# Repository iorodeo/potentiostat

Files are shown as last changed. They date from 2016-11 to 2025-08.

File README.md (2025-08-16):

# IO Rodeo Rodeostat 

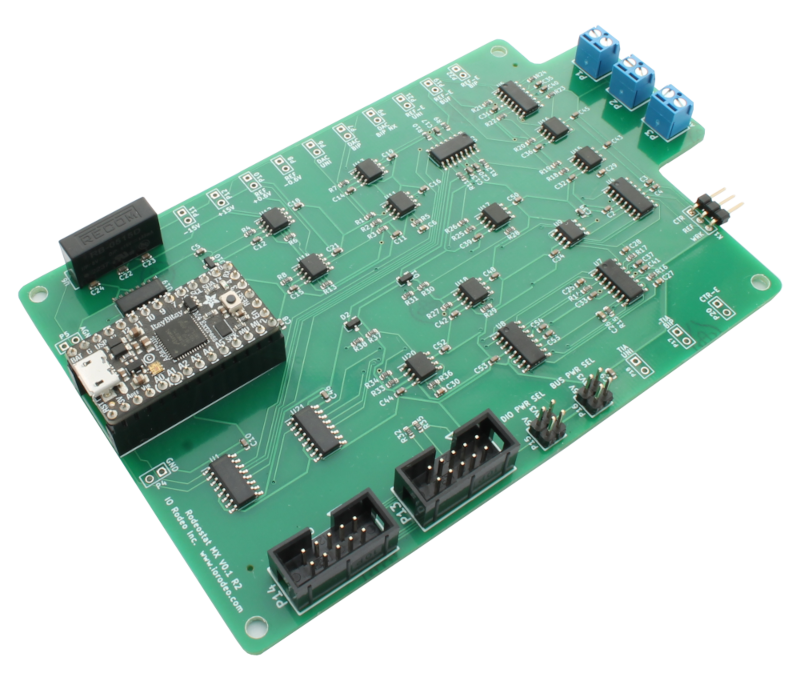
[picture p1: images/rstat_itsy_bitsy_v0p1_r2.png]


Hardware design, firmware and software for IO Rodeo's Rodeostat Potentiostat. 

* Project site: http://potentiostat.iorodeo.com 

## Hardware

* Designed as a shield for  [teensy 3.2 development board](https://www.pjrc.com/teensy/teensy31.html).   
* 12-bit voltage output with four range settings:  +/- 1, 2, 5, 10V
* 16-bit current measurement with four  range settings: +/- 1, 10, 100, 1000 uA ranges
* Can be programmed over USB using the Arduino IDE ([teensyduino](https://www.pjrc.com/teensy/td_download.html)).  
* Expansion headers with DIO, analog inputs, UART, I2C, and SPI 
* [Schematic](https://github.com/iorodeo/potentiostat/releases/download/v0.1/potentiostat_shield_schematic_v0p1r2.pdf)

## Firmware

* Implements many standard voltammetric methods including: 
    - constant voltage, 
    - cyclic voltammetry, 
    - sinusoidal voltammetry,
    - linearsweep voltammetry, 
    - chronoamperometry, 
    - multistep. 
* API for control over USB/Serial using messages in JSON. 
* Easy to extend enabling users to add custom tests. 

## Libraries

* Python 
    - Documentation https://iorodeo.github.io/iorodeo-potentiostat-docs-build/

## Software

* Web app
    - Documentation https://blog.iorodeo.com/rodeostat-software/

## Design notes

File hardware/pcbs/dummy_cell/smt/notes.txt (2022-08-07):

Surface mount right angle header 0.1" pitch.  Part #BG300-03-A-L-A

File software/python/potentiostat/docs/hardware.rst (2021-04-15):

################
Hardware Summary 
################

* teensy 3.2 (32-bit ARM Cortex-M4 72 MHz CPU, 256k Flash, 64k RAM, 2K EEPROM)
* 12-bit voltage output with four available ranges:   ±1, 2, 5, 10V
* 16-bit current measurement with four available ranges: ±1, 10, 100, 1000uA
* Controlled over USB using simple JSON messages  
* Can be programmed over USB using the Arduino IDE (`teensyduino <https://www.pjrc.com/teensy/td_download.html>`_).  
* Expansion headers with DIO, analog inputs, UART, I2C, and SPI 
* Firmware supports many standard voltammetric methods including:
    * constant voltage
    * cyclic voltammetry
    * sinusoidal voltammetry 
    * linear sweep voltammetry
    * chronoamperometry
    * multistep

For a more detailed description of the device hardware see (TODO)

*********
Schematic
*********
`download pdf <https://github.com/iorodeo/potentiostat/releases/download/v0.1/potentiostat_shield_schematic_v0p2r1.pdf>`_

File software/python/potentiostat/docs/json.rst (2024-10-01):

.. _json_ref:

############################
JSON Serial Commands
############################

All messages sent between the Rodeostat and the host PC are sent as serialized
JSON.  This section provides a brief introduction to to these commands and the
associated responses to the command returned by the device. 

.. note::

    The Potentiostat class provides a high level interface implementing this
    protocol - so you don't need to know the details of the JSON serial
    commands in order to use the Rodeostat with Python. We provide the details
    here in order ot enable a more complete understand of how the device
    functions and to assist those who wishing to develop their own custom
    programming interfaces with the Rodeostat. 

The basic form of the commands sent from the host PC to the Rodeostat are JSON
objects with the key "command" whose value specifies the name of the command.
Additional arguments, which are specific to the command, are given as key/value
pairs. The names and number of the required additional arguments are specific 
to each command. 

.. code-block:: json

    {"command": "command name", "arg1": "val1", "arg2": "val2"}

The response from the device, in turn, is a JSON object containing a key named
"success" whose value is a boolean specifying whether or not the command was
successful. If the command was successful the boolean value will be true and
the object will contain a key named "response" whose value contains the
response from the device. The response itself consists of a number of key/value
pairs which are specific to the command. However, reposonse will always contain
the key "command" whose value specifies the name of the command generating the
response. 

.. code-block:: json

    {"success": true, "response", {"command": "command name", "key1": "val1", "key2": "val2"}}

On the other hand if the command was unsuccessful the boolean value will be
false and the object will contain the key "message" whose value contains an
error message from the device. 

.. code-block:: json

    {"success": false, "message": "error message from device", "response": {}}

List of commands
################

getVariant
    Returns a string representing the hardware variant
    
    Form:
    
    .. code-block:: 

        {CommandKey: GetVariantCmd}

    Example command:

    .. code-block:: json
    
        {"command":"getVariant"}

    Example response:
    
    .. code-block:: json
    
        {"success":true,"response":{"command":"getVersion","version":"FW0.0.9"}}

stopTest
    Stops (any) currently running tests

    Form: 

    .. code-block:: 
    
        {CommandKey: StopTestCmd}

    Example command

    .. code-block:: json

        {"command":"stopTest"}

    Example response:

    .. code-block:: json

        {"success":true,"response":{"command":"stopTest"}}

getVolt
    Returns the output voltage setting, i.e, the potential between the working
    and reference electrode. 

    Form: 
    
    .. code-block:: 
    
        {CommandKey: GetVoltCmd}

    Example command:

    .. code-block:: json

        {"command":"getVolt"}

    Response:

    .. code-block:: json

        {"success":true,"response":{"command":"getVolt","v":-0.000244}}

setVolt
    Sets the output voltage setting, i.e., the potential between the working
    and reference electrode. 

    Form: 
    
    .. code-block:: 
    
        {CommandKey: SetVoltCmd, VoltKey: volt}

    Example command:

    .. code-block:: json

        {"command":"setVolt", "v": 0.5}

    Example response:

    .. code-block:: json

        {"success":true,"response":{"command":"setVolt","v":0.499878}}

getCurr
    Gets an immediate measurement of the working electrode current. 

    Form: 
    
    .. code-block:: 
    
        {CommandKey: GetCurrCmd}

    Example command:

    .. code-block:: json

        {"command": "getCurr"}

    Example response:

    .. code-block:: json

        {"success":true,"response":{"command":"getCurr","i":-0.095238}}

getRefVolt
    Gets an immediate measurement of the potential between the working and
    reference electrode. 

    Form: 
    .. code-block:: 
        
        {CommandKey: GetRefVoltCmd}

    Example command:
    
    .. code-block:: json

        {"command": "getRefVolt"}

    Example response:
    
    .. code-block:: json
    
        {"success":true,"response":{"command":"getRefVolt","r":0.761661}}

getParam
    Returns the current values of the parameters for the specified
    voltammetric test. 

    Form: 
    
    .. code-block:: 
    
        {CommandKey: GetParamCmd, TestKey: testname} 

    Example command:

    .. code-block:: json
    
        {"command": "getParam", "test": "cyclic"}

    Example response:
    
    .. code-block:: json
    
        { 
            "success":true,
            "response": {
                "command":"getParam",
                "test":"cyclic",
                "param":{
                    "quietValue":0,
                    "quietTime":0,
                    "amplitude":1,
                    "offset":0,
                    "period":1000,
                    "numCycles":10,
                    "shift":0 
                }
            }
        }

setParam
    Sets the parameters for the specified voltammetric test.

    Form: 
    
    .. code-block:: 

        {CommandKey: SetParamCmd, TestKey: testname, ParamKey: param}

    Example command: 
    
    .. code-block:: json
    
        {
            "command": "setParam",  
            "test": "cyclic",  
            "param": {
                "quietValue": -0.1,
                "quietTime": 1000,
                "amplitude": 1.5,
                "offset": 0,
                "period": 1000,
                "numCycles": 10,
                "shift": 0
            }
        }

    Example response:
    
    .. code-block:: json
    
        {
            "success": true,
            "response": {
                "command": "setParam",
                "test": "cyclic",
                "param": {
                    "quietValue": -0.1,
                    "quietTime": 1000,
                    "amplitude": 1.5,
                    "offset": 0,
                    "period": 1000,
                    "numCycles": 10, 
                    "shift": 0
                }
            }
        }

setVoltRange
    Sets the output voltage range (V)- used when setting output voltage
    manually.

    Form: 

    .. code-block:: 

        {CommandKey: SetVoltRangeCmd, VoltRangeKey: volt_range} 

    Example command:
    
    .. code-block:: json
    
        {"command":"setVoltRange", "voltRange": "2V"}

    Example response:
    
    .. code-block:: json
    
        {"success":true,"response":{"command":"setVoltRange","voltRange":"2V"}}

getVoltRange
    Gets the current value for the output voltage range (V).

    Form: 
    
    .. code-block:: 
        
        {CommandKey: GetVoltRangeCmd}

    Example command:
    
    .. code-block:: json
    
        {"command":"getVoltRange"}

    Example response:
    
    .. code-block:: json
    
        {"success":true,"response":{"command":"getVoltRange","voltRange":"2V"}}

setCurrRange
    Sets the range setting for measuring working electrode (uA).

    Form: 
    
    .. code-block:: 
    
        {CommandKey: SetCurrRangeCmd, CurrRangeKey: curr_range}

    Example command:
    
    .. code-block:: json
    
        {"command":"setCurrRange", "currRange": "100uA"}

    Example response:
    
    .. code-block:: json
    
        {"success":true,"response":{"command":"setCurrRange","currRange":"100uA"}}

getCurrRange:
    Gets the device's range setting for measuring working electrode current (uA).

    Form: 
    
    .. code-block:: 
    
        {CommandKey: GetCurrRangeCmd}

    Example command:
    
    .. code-block:: json
    
        {"command":"getCurrRange"}

    Example response:
    
    .. code-block:: json
    
        {"success":true,"response":{"command":"getCurrRange","currRange":"100uA"}}

getDeviceId
    Gets the current value of the device identification number

    Form: 
    
    .. code-block:: 

        {CommandKey: SetDeviceIdCmd, DeviceIdKey: device_id}

    Example command:
    
    .. code-block:: json
    
        {"command":"getDeviceId"}

    Example response:
    
    .. code-block:: json
    
        {"success":true,"response":{"command":"getDeviceId","deviceId":0}}

setDeviceId
    Sets the current value of the device identification number.

    Form: 
    
    .. code-block:: 

        {CommandKey: SetDeviceIdCmd, DeviceIdKey: device_id}

    Example command:
    
    .. code-block:: json
    
        {"command":"setDeviceId", "deviceId": 1}

    Example response:
    
    .. code-block:: json
    
        {"success":true,"response":{"command":"setDeviceId","deviceId":1}}

setSamplePeriod
    Sets the sample period (ms) used for measurements. The sample period is
    the time between samples. 

    Form: 
    
    .. code-block:: 
    
        {CommandKey: SetSamplePeriodCmd, SamplePeriodKey: sample_period}

    Example command:
    
    .. code-block:: json
    
        {"command":"setSamplePeriod", "samplePeriod": 20}

    Example response:
    
    .. code-block:: json
    
        {"success":true,"response":{"command":"setSamplePeriod","samplePeriod":20}}

getSamplePeriod
    Gets the current value for the sample period (ms). The sample period is
    the time between samples.

    Form: 
    
    .. code-block:: 

        {CommandKey: GetSamplePeriodCmd}

    Example command:
    
    .. code-block:: json
    
        {"command":"getSamplePeriod"}

    Example response:
    
    .. code-block:: json
    
        {"success":true,"response":{"command":"getSamplePeriod","samplePeriod":20}}

getTestDoneTime
    Gets the time in milliseonds required to complete the specified test including
    any quietTime, etc. 

    Form: 
    
    .. code-block:: 
    
        {CommandKey: GetTestDoneTimeCmd, TestKey: test}

    Example command:
    
    .. code-block:: json
    
        {"command": "getTestDoneTime", "test": "cyclic"}

    Example response:
    
    .. code-block:: json
    
        {
            "success": true,
            "response": {
                "command": "getTestDoneTime",
                "test": "cyclic",
                "testDoneTime": 11000
            }
        }

getTestNames
    Gets the list of the names of all tests which can be performed by the
    device with the current firmware. 

    Form: 
    
    .. code-block:: 

        {CommandKey: GetTestNamesCmd}

    Example command:
    
    .. code-block:: json
    
        {"command": "getTestNames"}

    Example response:
    
    .. code-block:: json
    
        {
            "success": true,
            "response": {
                "command": "getTestNames",
                "testNames": ["cyclic","sinusoid","constant","squareWave","linearSweep","chronoamp","multiStep"]
            }
        }

getVersion
    Gets the version string for the firmware on the device.

    Form: 
    
    .. code-block:: 
    
        {CommandKey: GetVersionCmd}

    Example command:
    
    .. code-block:: json
    
        {"command": "getVersion"}

    Example response:
    
    .. code-block:: json
    
        {"success":true,"response":{"command":"getVersion","version":"FW0.0.9"}}

getHardwareVersion 
    Returns string representing the hardware version.

    Form: 
     
    .. code-block:: 
     
        {CommandKey: GetHardwareVersionCmd}

    Example command:
     
    .. code-block:: json
     
        {"command": "getHardwareVersion"}

    Example response:
     
    .. code-block:: json
     
        {"success":true,"response":{"command":"getHardwareVersion","version":"V0.2"}}

setRefElectConnected
    Sets the connected state (True/False) of the reference electrode.  This
    feature requires hardware version >= HW0.2

    Form: 
    
    .. code-block:: 
    
        {CommandKey: SetRefElectConnCmd, ConnectedKey: value}

    Example command:
    
    .. code-block:: json
    
        {"command": "setRefElectConnected", "connected": true}

    Example response:
    
    .. code-block:: json
    
        {"success":true,"response":{"command":"setRefElectConnected","connected":true}}

getRefElectConnected
    Gets the connected state (True/False) of the reference electrode.  This
    feature requires hardware version >= HW0.2

    Form: 
    
    .. code-block:: 
    
        {CommandKey: GetRefElectConnCmd}

    Example command:
    
    .. code-block:: json
    
        {"command": "getRefElectConnected"}

    Example response:
    
    .. code-block:: json
    
        {"success":true,"response":{"command":"getRefElectConnected","connected":true}}

setCtrElectConnected
    Sets the connected state (True/False) of the counter electrode.  This
    feature requires hardware version >= HW0.2

    Form: 
    
    .. code-block:: 
    
        {CommandKey: SetCtrElectConnCmd, ConnectedKey: value}

    Example command:
    
    .. code-block:: json
    
        {"command": "setCtrElectConnected", "connected": true}

    Example response:
    
    .. code-block:: json
    
        {"success":true,"response":{"command":"setCtrElectConnected","connected":true}}

getCtrElectConnected
    Gets the connected state (True/False) of the counter electrode.  This
    feature requires hardware version >= HW0.2

    Form:  
    
    .. code-block:: 
    
        {CommandKey: GetCtrElectConnCmd}

    Example command:
    
    .. code-block:: json
    
        {"command": "getCtrElectConnected"}

    Example response:
    
    .. code-block:: json
    
        {"success":true,"response":{"command":"getCtrElectConnected","connected":true}}

setWrkElectConnected
    Sets the connected state (True/False) of the working electrode.  This
    feature requires hardware version >= HW0.2

    Form:  
    
    .. code-block:: 
    
        {CommandKey: SetWrkElectConnCmd, ConnectedKey: value}

    Example command:
    
    .. code-block:: json
    
        {"command": "setWrkElectConnected", "connected": true}

    Example response:
    
    .. code-block:: json
    
        {"success":true,"response":{"command":"setWrkElectConnected","connected":true}}

getWrkElectConnected
    Gets the connected state (True/False) of the working electrode.  This
    feature requires hardware version >= HW0.2

    Form: 
    
    .. code-block:: 
    
        {CommandKey: GetWrkElectConnCmd}

    Example command:
    
    .. code-block:: json
    
        {"command": "getWrkElectConnected"}

    Example resposnse:
    
    .. code-block:: json
    
        {"command": "getWrkElectConnected"}

setAllElectConneced
    Sets the connected state (True/False) of all the electrodes (referene,
    counter and working). This feature requires hardware version >= HW0.2 

    Form: 
    
    .. code-block:: 
    
        {CommandKey: SetAllElectConnCmd, ConnectedKey: value}

    Example command:
    
    .. code-block:: json
    
        {"command": "setAllElectConnected", "connected": true}

    Example response:
    
    .. code-block:: json
    
        {"success":true,"response":{"command":"setAllElectConnected","connected":true}}

getAllElectConnected
    Gets the connected state (True/False) of all the electrodes (referene,
    counter and working). Only True if all are connected. This feature
    requires hardware version >= HW0.2

    Form: 
    
    .. code-block:: 
    
        {CommandKey: GetAllElectConnCmd}

    Example command:
    
    .. code-block:: json
    
        {"command": "getAllElectConnected"}

    Example response:
    
    .. code-block:: json
    
        {"success":true,"response":{"command":"getAllElectConnected","connected":true}}

setElectAutoConnect
    Set auto-connect/auto-disconnect feature. If auto-connect is set to True
    then the  ref, ctr and wrk electrodes will be automatically connected at
    the beginning of each test and automatically disconnected at the end of
    each test.

    Form: 
    
    .. code-block:: 
    
        {CommandKey: SetElectAutoConnCmd, AutoConnectKey: value}

    Example command:
    
    .. code-block:: json
    
        {"command": "setElectAutoConnect", "autoConnect": true}

    Example response:
    
    .. code-block:: json
    
        {"success":true,"response":{"command":"setElectAutoConnect","autoConnect":true}}

getElectAutoConnect
    Gets the value of the device's auto-connect/auto-disconnect setting.

    Form: 

    .. code-block:: 
    
        {CommandKey: GetElectAutoConnCmd}

    Example command:
    
    .. code-block:: json
    
        {"command": "getElectAutoConnect"}

    Example response:
    
    .. code-block:: json
    
        {"success":true,"response":{"command":"getElectAutoConnect","autoConnect":true}}

setRefElectVoltRange
    Sets the voltage range for the reference electrode analog input.

    Form: 

    .. code-block:: 
    
        {CommandKey: SetRefElectVoltRangeCmd, VoltRangeKey: volt_range}

    Example command:
    
    .. code-block:: json
    
        {"command": "setRefElectVoltRange", "voltRange": "2V"}

    Example response:
    
    .. code-block:: json
    
        {"success":true,"response":{"command":"setRefElectVoltRange","voltRange":"2V"}}

getRefElectVoltRange
    Gets the  device's voltage range setting for the reference electrode
    analog input.  

    Form: 
    
    .. code-block:: 

        {CommandKey: GetRefElectVoltRangeCmd}

    Example command:
    
    .. code-block:: json
    
        {"command": "getRefElectVoltRange"}

    Example response:
    
    .. code-block:: json
    
        {"success":true,"response":{"command":"getRefElectVoltRange","voltRange":"5V"}}

runTest
    Runs the test with specified test name and returns the time, voltage and
    current data.

    Form: 
    
    .. code-block:: 
    
        {CommandKey: RunTestCmd, TestKey: testname}

    Example command:
    
    .. code-block:: json
    
        {"command": "runTest", "test": "cyclic"}

    Example response:

    .. code-block:: json
    
        {"success":true,"response":{"command":"runTest","test":"cyclic"}}

    followed by streaming data 

    .. code-block:: json

        {"t":20,"v":-0.1,"i":-2.799983}
        {"t":40,"v":-0.1,"i":-2.8295}
        {"t":60,"v":-0.1,"i":-2.936976}
        {"t":80,"v":-0.1,"i":-2.782137}

    ... etc

    .. code-block:: json

        {"t":10980,"v":-1.38,"i":-28.1935}
        {"t":11000,"v":-1.5,"i":-30.62896}
        {}

    An empty object marks the end of the stream

**TO DO ... MUX commands**

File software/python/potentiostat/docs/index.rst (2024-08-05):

.. iorodeo-potentiostat documentation master file, created by
   sphinx-quickstart on Fri Mar 24 10:38:13 2017.
   You can adapt this file completely to your liking, but it should at least
   contain the root `toctree` directive.

####################
iorodeo-potentiostat  
####################

A Python library for controlling IO Rodeo's Rodeostat open source potentiostat

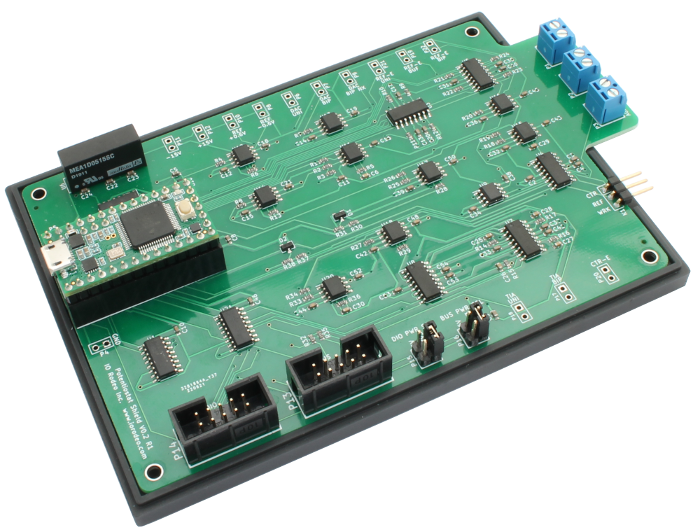
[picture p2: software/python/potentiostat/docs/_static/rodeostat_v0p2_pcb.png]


IO Rodeo's Rodeostat is an open source potentiostat for performing
electrochemical measurments which is designed to work with the `teensy 3.2
development board <https://www.pjrc.com/teensy/teensy31.html>`_. 
The **iorodeo-potentiostat** library provides a simple highlevel intreface for
controlling the Rodeostat allowing users to easily:  

* set/get the parameters used for the voltammetric tests
* run voltammetric tests and collect data from the device (time, voltage, current)
* set/get the output voltage and current measurement ranges
* set/get the sample rate/period used for measurements

To quickly get up and running using the library see the :ref:`getting_started_ref` guide.
For a more comprehensive coverage of the API provided by the library see the :ref:`api_ref`.

Contents:

.. toctree::
    :maxdepth: 2

    installation
    getting_started
    multiplexer
    examples
    tests 
    api_reference
    hardware
    json

******************
Indices and tables
******************

* :ref:`genindex`
* :ref:`modindex`
* :ref:`search`

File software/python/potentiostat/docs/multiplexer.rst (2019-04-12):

.. _multiplexer_ref:

############################
Multiplexer Exapansion Board
############################

This section provides a short guide to help you begin using your Rodeostat in
conjunction with the multiplexer expansion board.  This  expansion board
enables the Rodeostat to use up to seven independent working electrodes
simultaneously. When connected to the Rodeostat additional features provided
multiplexer may accessed programmatically via the Python API. 

**********************************
Enabling/Disabling the multiplexer
**********************************

In order to use the multiplexer it must first be enabled. This can be done
using the :meth:`~potentiostat.Potentiostat.set_mux_enabled` method. To enable the 
multiplexer you would run the following command 

.. code-block:: python

  rsp = pstat.set_mux_enabled(True)

Similarly in order to disable the multiplexer you would run the command shown below

.. code-block:: python

  rsp = pstat.set_mux_enabled(False)

The response returned by the :meth:`~potentiostat.Potentiostat.set_mux_enabled`
will be either True/False indicating whether or not the multiplexer has been
successfully enabled/disabled respectively. 

***************************************
Setting the working electrode channels
***************************************

The multiplexer has seven working electrode channels. You don't need to use all
the working electrode channels and the same time. The subset of working
electrode channel which are enabled can be set using the
:meth:`~potentiostat.Potentiostat.set_enabled_mux_channels` method. For example,
the following command will enable working electrode channels 1, 3 and 7.

.. code-block:: python

  pstat.set_enabled_mux_channels([1,3,7])

To query the device for the list of currently enabled working electrode
channels you can using the
:meth:`~potentiostat.Potentiostat.get_enabled_mux_channels` method. For example
the command

.. code-block:: python

  channel_list = pstat.get_enabled_mux_channels()

In order to run a test with the multiplexer expansion board the firmware requires 
that at least one working electrode channel is enabled.  

***************************************
Running tests
***************************************

Running tests with the multiplexer expansion board enabled is almost exactly
the same as normal using the :meth:`~potentiostat.Potentiostat.run_test`
method.  For example, in order to run the cyclic voltammetry test you could do
the following. 

.. code-block:: python

   data_dict = pstat.run_test('cyclic')

The main difference is that when the multiplexer is enabled the
:meth:`~potentiostat.Potentiostat.run_test` returns a dictionary containing the
measured data for each channel rather than a tuple of times, voltages and
currents.  The keys of the dictionary returned are the enabled channel numbers
and the values are dictionaries with the time, voltage and current measurments
for that channel, keyed by 't', 'v', and 'i' respectively.  Thus the time,
voltage and current data for channel 1 can be accessed as follows.

.. code-block:: python

    chan1_time = data_dict[1]['t']  # channel 1, list of sample times 
    chan1_volt = data_dict[1]['v']  # channel 1, list of output voltages
    chan1_curr = data_dict[1]['i']  # channel 1, list of current samples 

The parameters for the test can be set as usual using the
:meth:`~potentiostat.Potentiostat.set_param` method as described in the
:ref:`getting_started_set_param_ref` subsection, or by specifying the
parameters using the params keyword argument to the
:meth:`~potentiostat.Potentiostat.run_test` method as shown below

.. code-block:: python

    my_param = { 
        'quietValue' : 0.0,
        'quietTime'  : 1000,
        'amplitude'  : 2.0,
        'offset'     : 0.0,
        'period'     : 1000,
        'numCycles'  : 5,
        'shift'      : 0.0, 
        }

    data_dict  = pstat.run_test('cyclic', param=my_param)

.. note::

    When using the multiplexer all electrodes (counter, reference and working)
    are on digitally controlled switches.  By default, when not running a test,
    the electrodes will be disconnected. When using the
    :meth:`~potentiostat.Potentiostat.run_test` method the electrodes will be
    automatically connected using these switches prior to running the test.
    Similarly, after the test is complete, the electrodes will be automatically
    disconnected. 

.. note::

    At this time the squareWave test is not compatible with the multiplexer
    expansion board. Attempting to run this when the multiplexer is enabled
    will result in an error. 

To get a list of the test which are compatibile with the multiplexer the 
:meth:`~potentiostat.Potentiostat.get_mux_test_names`  can be used.

.. code-block:: python
    
    test_names = pstat.get_mux_test_names()

This command will return a list such as that shown below

.. code-block:: python

  test_names = ['cyclic', 'sinusoid', 'constant', 'linearSweep', 'chronoamp', 'multiStep']

***************************************************
Manual/direct operation when the multiplexer 
***************************************************

When using the Rodeostat with the multiplexer expansion board in manual/direct
control mode a few special considerations are required.  By default all
electrodes (counter, reference and working) are disconnected and you must
manually specify in software when you want to connect a specific electrode. 
The methods used for the reference and counter electrodes this are:

    * :meth:`~potentiostat.Potentiostat.set_mux_ctr_elect_connected` which connects/disconnects the counter electrode 
    * :meth:`~potentiostat.Potentiostat.set_mux_ref_elect_connected` which connects/disconnects the reference electrode 

For example, the following commmands connect the counter and reference electrodes.

.. code-block:: python

    pstat.set_mux_ctr_elect_connected(True)   # connect the counter electrode 
    pstat.set_mux_ref_elect_connected(True)   # connect the reference electrode

Similarly, the counter and referece electrodes can be disconnected as shown below. 

.. code-block:: python

    pstat.set_mux_ctr_elect_connected(False)   # disconnect the counter electrode 
    pstat.set_mux_ref_elect_connected(False)   # disconnect the reference electrode

The enabled working electrodes are automatically connected to multiplexer. In
addition the working electrodes can be connected to current measurement
circuit (transimpedance amplifier) via the make-before-break multiplexer using the
:meth:`~potentiostat.Potentiostat.set_mux_wrk_elect_connected` method. This
command takes as an argument the number of the working electrode you would like
to connect to the measurement circuit. For example, to connect working
electrode number 3 to the current measurement circuit you would use the folling
command.

.. code-block:: python

    pstat.set_mux_wrk_elect_connected(3)  # connect working electrode number 3 to TIA 

.. note::

    Only one enabled working electrode can be connected to the
    measurement circuit at a time. For example, if working electrode number 3 is
    connected the the current measurement and you wish to connect working
    electrode 5 to this circuit you can do this by running the command 
    pstat.set_mux_wrk_elect_connected(5). This will connect working electrode 5
    to the measurement circuit. However, prior to connecting working electrode
    5, working electrode 3 will first be disconnected, using the a
    make-before-break protocol, before connecting electrode 5.

To disconnect all working electrodes from the measurement circuit the you can
run the :meth:`~potentiostat.Potentiostat.set_mux_wrk_elect_connected`  method
with an argument of False. For example, 

.. code-block:: python

    pstat.set_mux_wrk_elect_connected(False)  # disconnect all working electrodes from TIA 

.. note::

    When working electrodes are enabled the are connected electronically to the
    multiplexer (and Rodeostat). At this point the can sink/source current. The
    :meth:`~potentiostat.Potentiostat.set_mux_wrk_elect_connected` just selects
    which of the enabled working electrodes is connect to current measurent
    circuit (transimpedance amplifier) using the make-before-break protocol.

To disconnect all electrodes (counter, reference and working) with a single command the 
:meth:`~potentiostat.Potentiostat.disconnect_all_mux_elect` method  may be used as shown below.

.. code-block:: python

    pstat.disconnect_all_mux_elect()  # disconnect all electrodes

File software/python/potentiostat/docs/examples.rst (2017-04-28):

.. _examples_ref:

###############
Worked Examples
###############

In this section we show several worked examples demonstrating how to use iorodeo-potentiostat library
with your Rodeostat shield to make measurements. 

.. note::

   The examples in this section make use of the `Matplotlib`_ plotting library.
   You can find Instructions for installing maplotlib here: `installing Matplotlib`_.

******************
Cyclic voltammetry
******************

In the following example we demonstate how perform a `cyclic voltammetry`_ test with the following parameters:

* Starts and ends at minimum voltage of -100 mV . 
* Reaches a maximum voltage of 1000 mV at mid-cycle.
* Transistions at a rate of 50 mV/s (-50 mV/s) from the minimum (maximum) to the maximum (minimum) voltage.
* Performs a single cycle i.e., transistions from minimum to maximum and back to minimum exactly once.

As the test is run the data are saved to a file named *data.txt*. The data
in the file consist of comma separated values of time, voltage and current.
After the test is complete two figures are created to display the data. The
first figure shows plots of the voltage (potential) and current vs time. The
second figure shows a plot of the current vs the voltage (potential).

.. literalinclude:: ../examples/run_cyclic_w_plot.py
   :language: python 
   
An example of the data generated by running this test using a screen printed
electrode in a 8mM solution of ascorbate, is shown below.

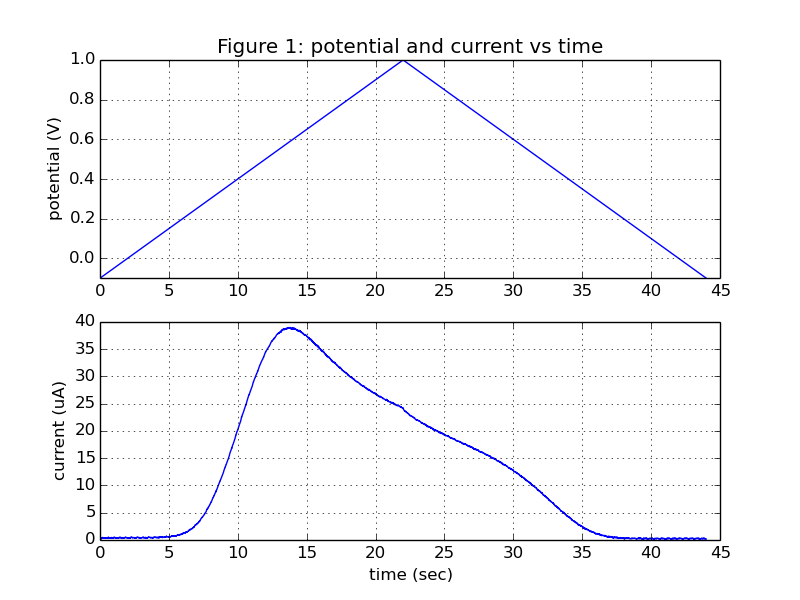
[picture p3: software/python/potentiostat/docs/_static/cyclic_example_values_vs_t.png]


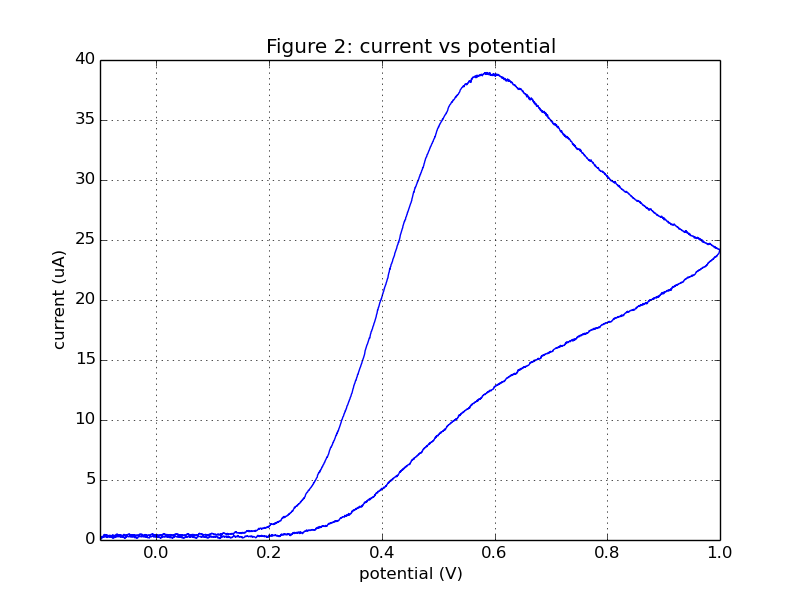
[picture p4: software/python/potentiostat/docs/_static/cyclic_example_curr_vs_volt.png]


Further details on the methods used for the ascorbate experiments can be found
here `http://potentiostat.iorodeo.com/methods`_.

****************************
Constant voltage voltammetry
****************************

This example demonstrates how to preform constant voltage voltammetry. The test parameters are as follows: 

* Prior to the start of the test a quiet period is used where the output voltage at 0V for 1s (1000ms). 
* During the test the output voltage is set to 2.5V and kept there for 4s (4000ms). 
* Data is acquired at a rate of 100 samples/second for the duration of the quiet period and the constant voltage test.

.. literalinclude:: ../examples/run_constant_w_plot.py
   :language: python 

Consider the dummy cell schematic show below.  We will use this dummy cell to
generate example data using the constant voltage test program (above).

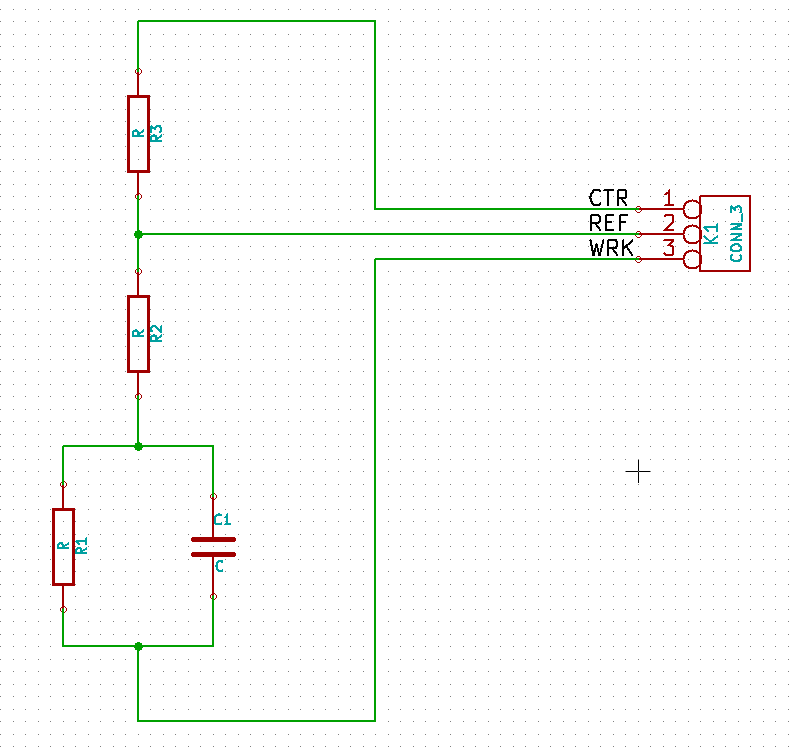
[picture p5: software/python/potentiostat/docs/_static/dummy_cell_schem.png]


There are three resistors  (R1, R2, R3) and one capacitor (C1) on the dummy
cell. In the example below, showing voltage and current vs time, the values of the resistors and capacitors are:
R1=100k, R2=50k, R3=0 Ohm (wire conductor), C1=4.7 uF. 

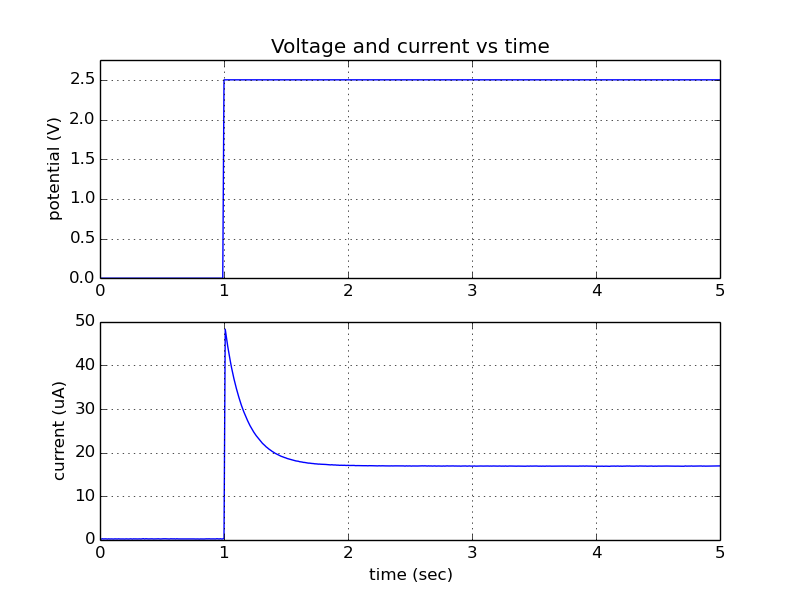
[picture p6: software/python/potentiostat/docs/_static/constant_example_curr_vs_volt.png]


During the one the 1 second quiet period the output voltage is 0 V.  After 1
second the actual test begins and the output voltage is set to 2.5 V. There an
initial spike in current at the start of the test. The current then decays
exponentially, as the capacitor C1 charges, gradually approaching a steady state
value.

**********************
Manual/direct control:  
**********************

In this section we give several examples which demostrate how to use the
Rodeostat  in manual/direct control mode. When using this mode,
the output voltage is set and the current is measured directly from the host PC
using the :meth:`~potentiostat.Potentiostat.set_volt` and
:meth:`~potentiostat.Potentiostat.get_curr` methods.  Note, the timing in
manual/direct control mode is determined by the software on the host PC and it
will not be as precise as when using a pre-programmed voltammetric test running
in firmware on the Teensy 3.2.  However, it does offer a great deal of
flexibility to the user and enables the creation of custom voltammetric test
without any firmware programming. 

Example 1: linear plus sinewave
================================

This example demonstrates how to use manual/direct control to create an output voltage 
which is sum of a linear function and a sine wave.  

.. literalinclude:: ../examples/manual_control_v2.py
   :language: python 

Example data generated using the program above for 50k dummy cell (R1=50k,
R2=R3=0 , C1=0) is shown below.  

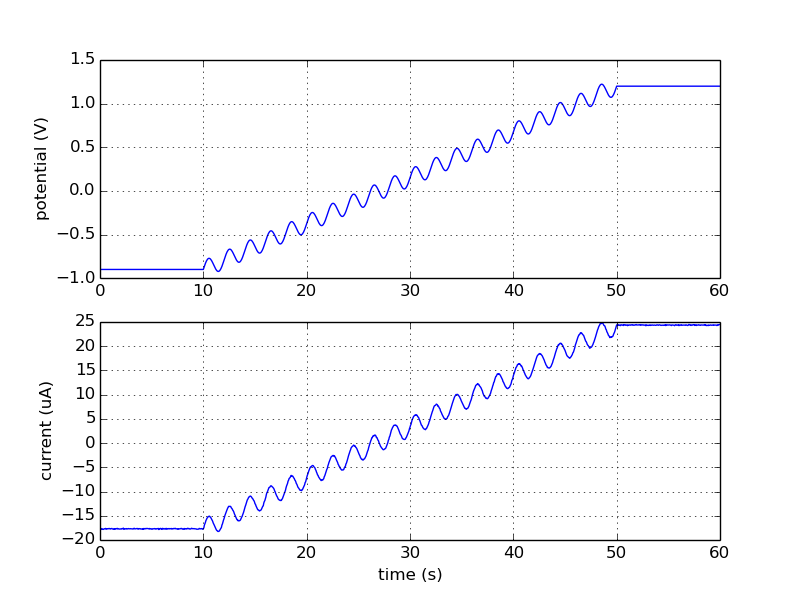
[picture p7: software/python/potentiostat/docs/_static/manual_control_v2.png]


In a similar manner you can easily create other custom tests by writing your
own custom voltage function which gives specifies the desired output voltage as
a function of time.

Example 2: long duration constant voltage test 
==============================================

Suppose you want to perform a very long duration (hours to days) constant
voltage test with the potentiostat. The sample rate for this test would be
fairly low - seconds to minutes between samples. In addition you wanted it such
that the logging application for this test could be interrupted and re-started
and any time.  

In the example below demonstrate how to use manual/direct control to create a
such a data logger for long duration constant voltage tests.  Once started, the
data logger shown below will run forever or until stopped by the user with
Ctl-C. The tests can be stopped and re-started and any time.  On restart if the
data logger finds an existing log file it will open this file and append data to it,
otherwise a new log file will be created. 

.. literalinclude:: ../examples/const_volt_logger.py
   :language: python 

**********
References
**********

.. target-notes::

.. _`Matplotlib`: http://matplotlib.org/ 
.. _`installing Matplotlib`: http://matplotlib.org/users/installing.html 
.. _`cyclic voltammetry`: https://en.wikipedia.org/wiki/Cyclic_voltammetry
.. _`http://potentiostat.iorodeo.com/methods`: http://potentiostat.iorodeo.com/methods

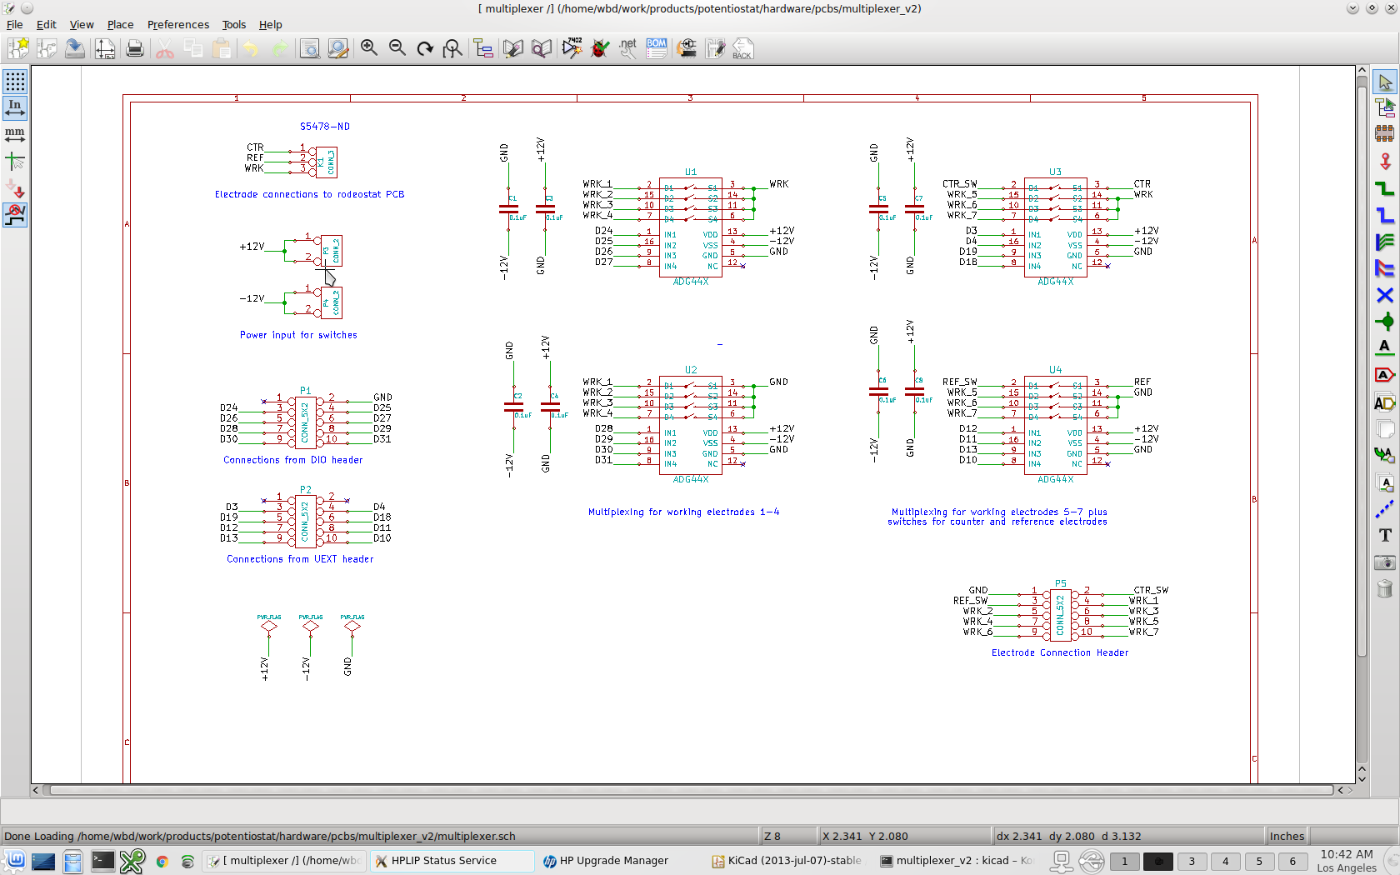
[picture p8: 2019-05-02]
hardware/pcbs/multiplexer_v0p2/schematic_screenshot.png

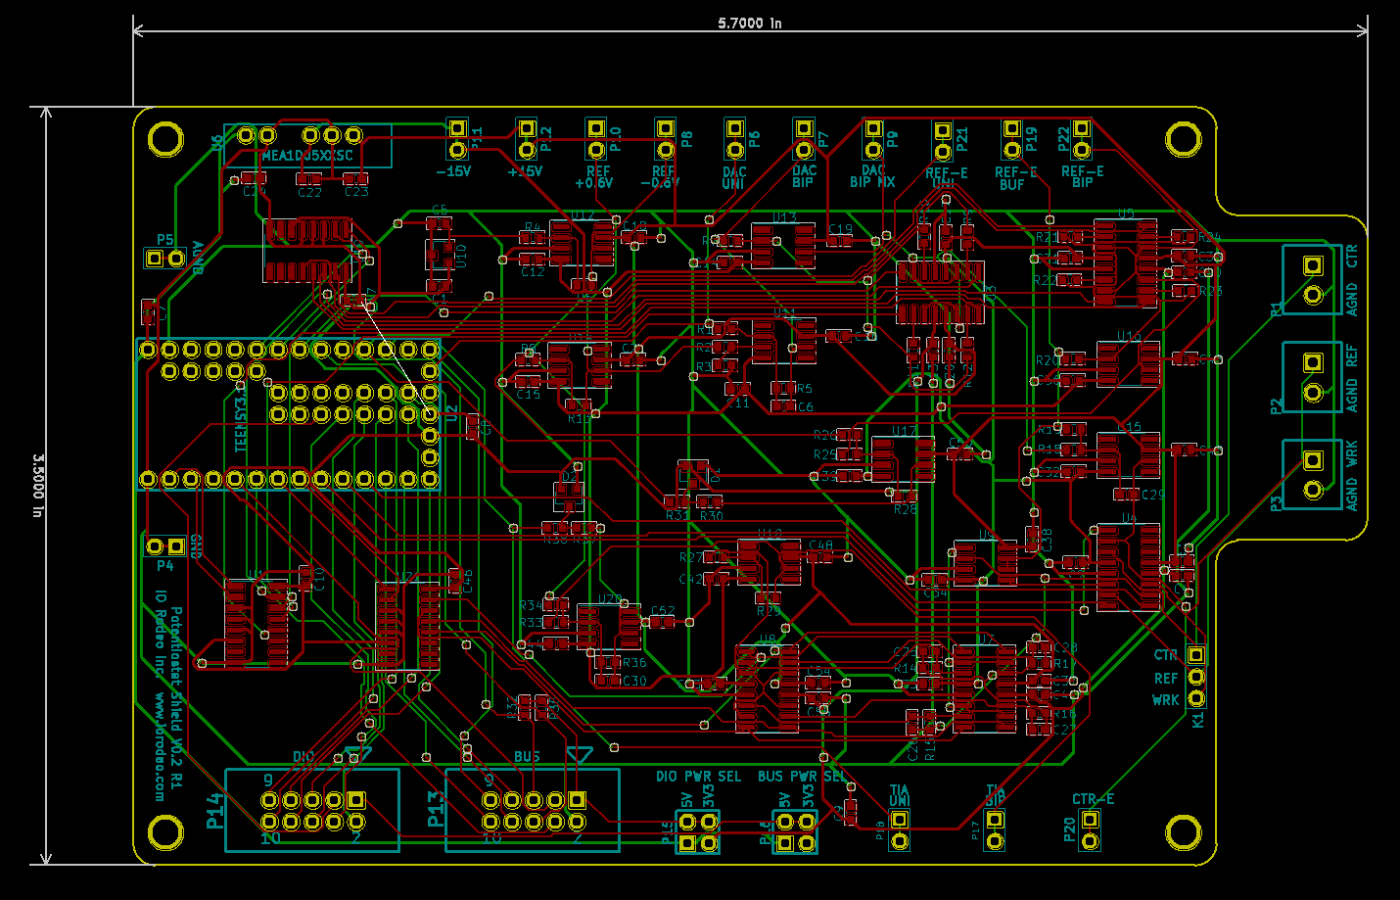
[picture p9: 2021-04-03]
hardware/pcbs/itsy_bitsy_mx_shield_v0p1/low_current/pcb_layout.png

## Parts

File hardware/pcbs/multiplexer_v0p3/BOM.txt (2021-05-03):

JLC PCB
=======

part      description                              vendor   PN                   qty   cost
--------------------------------------------------------------------------------------------
C1-C12    0.1uF ceramic capacitor, SM0603           LCSC    C14663               12    0.007 
U1-U4     DG411DY-T1-E3 Quad Analog Switches        LCSC    C17218                4    1.164   

Digikey
=======

part      description                              vendor   PN                   qty   cost
--------------------------------------------------------------------------------------------
K1        3-pin right angle connector              Digikey  S5478-ND              1    0.51
P1,P2 P5  5x2 shrouded header                      Digikey  S9169-ND              3    0.42
P3,P4     breakaway header                         Digikey  S1011EC-40-ND         1    0.66

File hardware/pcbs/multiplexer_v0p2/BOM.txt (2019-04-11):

part      description                              vendor   PN                   qty   cost
------------------------------------------------------------------------------------------
C1-C8     0.1uF ceramic capacitor, SM0805          Digikey  399-1176-1-ND         8    0.19
K1        3-pin right angle connector              Digikey  S5478-ND              1    0.51
P1,P2 P5  5x2 shrouded header                      Digikey  S9169-ND              3    0.42
P3,P4     breakaway header                         Digikey  S1011EC-40-ND         1    0.66
U1-U4     4 circuit IC switch                      Digikey  ADG441BRZ-REELCT-ND   4    2.89

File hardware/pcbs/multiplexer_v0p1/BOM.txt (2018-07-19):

part      description                              vendor   PN                   qty   cost
------------------------------------------------------------------------------------------
C1-C8     0.1uF ceramic capacitor, SM0805          Digikey  399-1176-1-ND         8    0.19
K1        3-pin right angle connector              Digikey  S5478-ND              1    0.51
K2,P5     term. block 3.5mm vert 3-pos             Digikey  ED2636-ND             2    1.00
P1,P2     5x2 shrouded header                      Digikey  S9169-ND              2    0.42
P3,P4     breakaway header                         Digikey  S1011EC-40-ND         1    0.66
P5        term. block 3.5mm vert 2-pos             Digikey  ED2635-ND             2    0.67
U1-U4     4 circuit IC switch                      Digikey  ADG441BRZ-REELCT-ND   4    2.89

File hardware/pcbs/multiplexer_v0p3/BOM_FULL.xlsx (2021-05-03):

JLCPCB
Comment | Designator | Footprint | LCSC Part #（optional） | Qty
0.1uF ceramic capacitor | C1,C2,C3,C4,C5,C6,C7,C8,C9,C10,C11,C12 | 603 | C14663 | 12
DG411DY-T1-E3 Quad Analog Switches | U1,U2,U3,U4 | SOIC-16_3.9x9.9x1.27P | C17218 | 4
Digikey
Comment | Designator | Footprint | Digikey Part #（optional） | Qty
3-pin right angle connector, femal | K1 | NA | S5478-ND | 1
5x2 shrouded header | P1, P2, P5 | NA | S9169-ND | 3
breakaway header | P3, P4 | NA | S1011EC-40-ND | 2

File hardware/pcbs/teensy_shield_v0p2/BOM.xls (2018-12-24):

Item # | Qty | Reference | Description | Package | PN | Vendor | Unit Cost | Cost
1 | 5 | C1, C5, C30, C37, C39 | 10nF capacitor | SM0805 | 311-1136-1-ND | Digikey | 0.1 | 0.5
2 | 4 | C19, C20, C21, C22 | 56nF capacitor | SM0805 | 478-1392-1-ND | Digikey | 0.15 | 0.6
3 | 17 | C2, C6, C10, C11, C12, C13, C14, C15, C17, C23, C24, C25, C27, C28, C33, C34, C35 | 0.1uF capacitor | SM0805 | 311-1361-1-ND | Digkey | 0.1 | 1.7
4 | 1 | C9 | 1.0uF capacitor | SM0805 | 1276-1066-1-ND | Digikey | 0.1 | 0.1
5 | 4 | C3, C7, C32, C38 | 4.7uF capacitor | SM0805 | 490-3335-1-ND | Digkey | 0.1 | 0.4
6 | 8 | C4, C8, C16, C18, C26, C29, C31, C36 | 10uF capacitor | SM0805 | 490-5523-1-ND | Digikey | 0.19 | 1.52
7 | 3 | P1, P2, P3 | 2-Pos. Term. Block, 3.5mm, Vert. | NA | ED2635-ND | Digikey | 0.43 | 1.29
8 | 1 | K1 | 3-pin right angle 0.1” pitch | NA | S1111EC-03-ND | Digikey | 0.22 | 0.22
9 | 2 | P13, P14 | 5x2 shrouded header, 0.1” | NA | S9169-ND | Digikey | 0.64 | 1.28
10 | 2 | P15, P16 | Conn. Header 4-Pos, 2 row, 0.1” | NA | 609-3201-ND | Digikey | 0.28 | 0.56
11 | 2 | R17, R19 | 100 Ohm resistor, tolerance 1% | SM0805 | 311-100CRCT-ND | Digikey | 0.1 | 0.2
12 | 1 | R4 | 191 Ohm resistor, tolerance 0.1% | SM0805 | P191DACT-ND | Digikey | 0.63 | 0.63
13 | 1 | R5 | 604 Ohm 0.1% resistor | SM0805 | P604DACT-ND | Digikey | 0.63 | 0.63
14 | 3 | R1, R15, R18 | 1k resistor, tolerance 1% | SM0805 | 311-1.00KCRCT-ND | Digikey | 0.1 | 0.3
15 | 2 | R12, R13 | 3k resistor, tolerance 0.1% | SM0805 | P3.0KDACT-ND | Digikey | 0.53 | 1.06
16 | 2 | R14, R16 | 4.7k resistor, tolerance 1% | SM0805 | 311-4.70KCRCT-ND | Digikey | 0.1 | 0.2
17 | 1 | R6 | 6.04K resistor 0.1% resistor | SM0805 | A110618CT-ND | Digikey | 0.61 | 0.61
18 | 2 | R2, R3 | 10k resistor | SM0805 | P10KDACT-ND | Digikey | 0.63 | 1.26
19 | 3 | R9, R10, R11 | 49.9k resistor, tolerance 0.1% | SM0805 | P49.9KDACT-ND | Digikey | 0.63 | 1.89
20 | 1 | R7 | 60.4k resistor, tolerance 0.1% | SM0805 | P60.4KDACT-ND | Digikey | 0.63 | 0.63
21 | 1 | R8 | 604k resistor, tolerance 0.1% | SM0805 | P604KDACT-ND | Digikey | 0.63 | 0.63
22 | 2 | D1, D2 | Diode Array, 1-pair series conn , Schottky | SOT23 | BAS70-04-E3-08 | Digikey | 0.4 | 0.8
23 | 1 | U1 | Shunt Voltage Reference IC | TSOT-23-5 | ZXRE060ET5DICT-ND | Digikey | 0.85 | 0.85 | 17.01
24 | 1 | U3 | Precision Voltage Reference (10V) | 8-SOIC | MAX6176AASA+-ND | Digikey | 4.57 | 4.57
25 | 2 | U4, U12 | Programmable Gain Amplifier | 10-MSOP | LT1995CMS#PBF-ND | Digikey | 3.79 | 7.58
26 | 1 | U5 | Programmable Gain Instrumentation Amplifier | 10-MSOP | AD8250ARMZ-R7CT-ND | Digikey | 10.98 | 10.98
27 | 1 | U6 | DC DC Converter 2 Output 12V -12V | 6-SIP Module (5 Leads) | 811-2678-5-ND | Digikey | 5.44 | 5.44
28 | 2 | U7, U8 | OPA129, General Purpose Amplifier | 8-SOIC | OPA129U-ND | Digikey | 7.2 | 14.4
29 | 2 | U9, U13 | 4 Circuit IC Switch | 16-SOIC | ADG441BRZ-REELCT-ND | Digikey | 2.55 | 5.1 |  | Substitution: | Digikey DG441DYZ-ND
30 | 1 | U10 | OPA227, General Purpose Amplifier | 8-SOIC | 296-26248-1-ND | Digikey | 3.25 | 3.25
31 | 1 | U11 | OP07x Precision Operational Amplifiers | 8-SOIC | 296-14626-1-ND | Digikey | 1.12 | 1.12 | 52.44
33 | 14 | P4, P5, P6, P7, P8, P9, P10, P11, P12, P17, P18, P19, P20, P21 | test point | NA | 923345-01-ND | Digikey | 0.1 | 1.4
34 | 1 | U2 | Surface mount header for Teensy 3.2 | NA | WM17453-ND | Digikey | 1.04 | 1.04
35 | 2 | U2 | 14 pos female header | NA | S7012-ND | Digikey | 1.14 | 2.28
36 | 2 | U2 | 5 pos female header | NA | S6103-ND | Digikey | 0.62 | 1.24
37 | 2 | U2 | 7 pos female header | NA | S7005-ND | Digikey | 0.78 | 1.56
38 | 1 | U2 | Teensy 3.2 | NA | DEV-13736 | Sparkfun | 19.95 | 19.95
 |  |  |  |  |  | Total w/o teensy |  | 69.18

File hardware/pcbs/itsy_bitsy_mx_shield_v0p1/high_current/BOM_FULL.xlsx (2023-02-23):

JLCPCB
Comment | Designator | Footprint | LCSC Part #（optional） | Qty
4.7uF ceramic capacitor | C5 | 603 | C19666 | 2
0.1uF ceramic capacitor | C2,C3,C4,C10,C11,C12,C13,C14,C15,C16,C17,C18,C19,C20,C21,C24,C31,C32,C33,C34,C35,C36,C37,C38,C39,C40,C41,C42,C43,C44,C45,C46,C47,C48,C50,C52,C53,C54,C55 | 603 | C14663 | 39
3.3nF ceramic capacitor | C6 | 603 | C170145 | 1
2.2uF ceramic capacitor | C7,C8,C9 | 603 | C23630 | 3
1uF ceramic capacitor | C22,C23 | 603 | C15849 | 2
56nF ceramic capacitor | C25,C26,C27,C28 | 603 | C31658 | 4
10nF ceramic capacitor | C29 | 603 | C57112 | 1
12nF ceramic capacitor | C30 | 603 | C1593 | 1
BAS70-04 Schottky Barrier Diodes | D1,D2 | SOT-23 | C609810 | 2
33k Resistor, 1% | R1,R2,R26,R28 | 603 | C4216 | 4
20k Resistor, 1% | R3,R4,R5,R8,R10,R13,R23,R25 | 603 | C4184 | 8
10k Resistor, 1% | R6,R7,R9,R18,R19,R24,R33,R34,R36 | 603 | C25804 | 9
49.9k Resistor, 1% | R11,R22 | 603 | C23184 | 2
100k Resistor, 1% | R12,R20,R21 | 603 | C25803 | 3
30k Resistor, 1% | R14 | 603 | C22984 | 1
3k Resistor, 1% | R15 | 603 | C4211 | 1
300 Ohm Resistor, 1% | R16 | 603 | C23025 | 1
30.1 Ohm Resistor, 1%, 200mW | R17 | 603 | C365143
2k Resistor, 1% | R27 | 603 | C22975 | 1
11k Resistor, 1% | R29 | 603 | C103227 | 1
1k Resistor, 1% | R30,R37 | 603 | C21190 | 2
100 Ohm Resistor | R31,R38 | 603 | C22775 | 2
4.7k Resistor | R32,R35 | 603 | C23162 | 2
74HC138 3-to-8 line decoder/demultiplexer | U1,U19,U21 | SOIC-16_3.9x9.9x1.27P | C5602 | 3
DG411DY-T1-E3 Quad Analog Switches | U3,U4,U5,U7,U8 | SOIC-16_3.9x9.9x1.27P | C17218 | 5
TL072CDT Dual JFET-Input Operational Amplifiers | U9 | SOIC-8_3.9x4.9x1.27P | C6961 | 1
OP07CDR Precision Operational Amplifier | U11,U12,U13,U14,U15,U16,U17,U18,U20 | SOIC-8_3.9x4.9x1.27P | C7433 | 9
Digikey
Comment | Designator | Footprint | Digikey Part #（optional） | Qty
3-pin right angle 0.1” pitch | K1 | NA | S1111EC-03-ND | 1
Break away header 40-pos 0.1” pitch | P1,P2,P3,P4,P5,P6,P7,P8,P9,P10,P11,P12,P17,P18,P19,P20,P21,P22 | NA | S1011EC-40-ND | 1
5x2 shrouded header, 0.1” | P13,P14 | NA | S9169-ND | 2
Header 4-Pos, 2 row, 0.1” | P15,P16 | NA | 609-3201-ND | 2
TEENSY3.2 | U2 | NA | 1568-1231-ND | 1
DC DC Converter 2 Output 15V -15V | U6 | NA | 811-2679-5-ND | 1
2-Pos. Term. Block, 3.5mm, Vert. | P1, P2, P2 | NA | ED2635-ND

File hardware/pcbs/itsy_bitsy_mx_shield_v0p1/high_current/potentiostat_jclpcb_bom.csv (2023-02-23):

Comment | Designator | Footprint | LCSC Part #
0.1uF Unpolarized capacitor | C2,C3,C4,C10,C11,C12,C13,C14,C15,C16,C17,C18,C19,C20,C21,C24,C31,C32,C33,C34,C35,C36,C37,C38,C39,C40,C41,C42,C43,C44,C45,C46,C47,C48,C50,C52,C53,C54,C55 | C_0603_1608Metric
4.7uF Unpolarized capacitor | C5 | C_0603_1608Metric | C19666
3.3nF Unpolarized capacitor | C6 | C_0603_1608Metric
2.2uF Unpolarized capacitor | C7,C8,C9 | C_0603_1608Metric
1uF Unpolarized capacitor | C22,C23 | C_0603_1608Metric
56nF Unpolarized capacitor | C25,C26,C27,C28 | C_0603_1608Metric
10nF Unpolarized capacitor | C29 | C_0603_1608Metric
12nF Unpolarized capacitor | C30 | C_0603_1608Metric
BAS07-04 | D1,D2 | SOT-23 | C609810
Conn_01x03 Generic connector, single row, 01x03, script generated (kicad-library-utils/schlib/autogen/connector/) | K1 | PIN_ARRAY_3X1
Conn_01x02 Generic connector, single row, 01x02, script generated (kicad-library-utils/schlib/autogen/connector/) | P1,P2,P3 | CONNBLOCK2
Conn_01x02 Generic connector, single row, 01x02, script generated (kicad-library-utils/schlib/autogen/connector/) | P4,P5,P6,P7,P8,P9,P10,P11,P12,P17,P18,P19,P20,P21,P22 | PIN_ARRAY_2X1
Conn_02x05_Odd_Even Generic connector, double row, 02x05, odd/even pin numbering scheme (row 1 odd numbers, row 2 even numbers), script generated (kicad-library-utils/schlib/autogen/connector/) | P13,P14 | 5X2_SHRD_HEADER
Conn_02x02_Odd_Even Generic connector, double row, 02x02, odd/even pin numbering scheme (row 1 odd numbers, row 2 even numbers), script generated (kicad-library-utils/schlib/autogen/connector/) | P15,P16 | PIN_ARRAY_2X2
33k Resistor | R1,R2,R26,R28 | R_0603_1608Metric
20k Resistor | R3,R4,R5,R8,R10,R13,R23,R25 | R_0603_1608Metric
10k Resistor | R6,R7,R9,R18,R19,R24,R33,R34,R36 | R_0603_1608Metric
50k Resistor | R11,R22 | R_0603_1608Metric
100k Resistor | R12,R20,R21 | R_0603_1608Metric
300k Resistor | R14 | R_0603_1608Metric
30k Resistor | R15 | R_0603_1608Metric
3k Resistor | R16 | R_0603_1608Metric
300 Resistor | R17 | R_0603_1608Metric
2k Resistor | R27 | R_0603_1608Metric
11k Resistor | R29 | R_0603_1608Metric
1k Resistor | R30,R37 | R_0603_1608Metric
100 Resistor | R31,R38 | R_0603_1608Metric
4.7k Resistor | R32,R35 | R_0603_1608Metric
74HC138 3-to-8 line decoder/demultiplexer; inverting, DIP-16/SOIC-16/SSOP-16 | U1,U19,U21 | SOIC-16_3.9x9.9mm_P1.27mm | C5602
ITSY_BITSY_M4 | U2 | ITSY_BITSY_M4
DG411xY Quad SPST Monolithic CMOS Analog Switches, normally ON, 17Ohm Ron, SOIC-16 | U3,U4,U5,U7,U8 | SOIC-16_3.9x9.9mm_P1.27mm | C17218
MEA1D05XXSC | U6 | MEA1
TL072 Dual Low-Noise JFET-Input Operational Amplifiers, DIP-8/SOIC-8 | U9 | SOIC-8_3.9x4.9mm_P1.27mm | C6961
OP07 Single Ultra-Low Offset Voltage Operational Amplifier, DIP-8/SOIC-8 | U11,U12,U13,U14,U15,U16,U17,U18,U20 | SOIC-8_3.9x4.9mm_P1.27mm | C7433

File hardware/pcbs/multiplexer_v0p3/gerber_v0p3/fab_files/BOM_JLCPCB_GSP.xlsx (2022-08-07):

Comment | Designator | Footprint | LCSC Part #（optional） | Qty
0.1uF ceramic capacitor | C1,C2,C3,C4,C5,C6,C7,C8,C9,C10,C11,C12 | 603 | C14663 | 12
DG411LEDY-T1-GE3 VISHAY SILICONIX | U1,U2,U3,U4 | SOIC-16_3.9x9.9x1.27P | DG411LEDY-T1-GE3 VISHAY SILICONIX | 4

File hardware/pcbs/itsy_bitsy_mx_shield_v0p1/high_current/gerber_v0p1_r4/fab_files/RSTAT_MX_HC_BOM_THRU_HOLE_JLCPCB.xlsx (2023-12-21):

Comment | Designator | Footprint | LCSC Part #（optional） | Qty
4.7uF ceramic capacitor | C5 | 603 | C19666 | 2
0.1uF ceramic capacitor | C2,C3,C4,C10,C11,C12,C13,C14,C15,C16,C17,C18,C19,C20,C21,C24,C31,C32,C33,C34,C35,C36,C37,C38,C39,C40,C41,C42,C43,C44,C45,C46,C47,C48,C50,C52,C53,C54,C55 | 603 | C14663 | 39
3.3nF ceramic capacitor | C6 | 603 | C170145 | 1
2.2uF ceramic capacitor | C7,C8,C9 | 603 | C23630 | 3
1uF ceramic capacitor | C22,C23 | 603 | C15849 | 2
56nF ceramic capacitor | C25,C26,C27,C28 | 603 | C31658 | 4
10nF ceramic capacitor | C29 | 603 | C57112 | 1
12nF ceramic capacitor | C30 | 603 | C1593 | 1
BAS70-04 Schottky Barrier Diodes | D1,D2 | SOT-23 | C609810 | 2
33k Resistor, 1% | R1,R2,R26,R28 | 603 | C4216 | 4
20k Resistor, 1% | R3,R4,R5,R8,R10,R13,R23,R25 | 603 | C4184 | 8
10k Resistor, 1% | R6,R7,R9,R18,R19,R24,R33,R34,R36 | 603 | C25804 | 9
49.9k Resistor, 1% | R11,R22 | 603 | C23184 | 2
100k Resistor, 1% | R12,R20,R21 | 603 | C25803 | 3
30k Resistor, 1% | R14 | 603 | C22984 | 1
3k Resistor, 1% | R15 | 603 | C4211 | 1
300 Ohm Resistor, 1% | R16 | 603 | C23025 | 1
30.1 Ohm Resistor, 1%, 200mW | R17 | 603 | C365143
2k Resistor, 1% | R27 | 603 | C22975 | 1
11k Resistor, 1% | R29 | 603 | C103227 | 1
1k Resistor, 1% | R30,R37 | 603 | C21190 | 2
100 Ohm Resistor | R31,R38 | 603 | C22775 | 2
4.7k Resistor | R32,R35 | 603 | C23162 | 2
74HC138 3-to-8 line decoder/demultiplexer | U1,U19,U21 | SOIC-16_3.9x9.9x1.27P | C6818 | 3
DG201BDY-T1-E3 Quad Analog Switches | U3,U4,U5,U7,U8 | SOIC-16_3.9x9.9x1.27P | C222535 | 5
TL072CDT Dual JFET-Input Operational Amplifiers | U9 | SOIC-8_3.9x4.9x1.27P | C6961 | 1
OP07CDR Precision Operational Amplifier | U11,U12,U13,U14,U15,U16,U17,U18,U20 | SOIC-8_3.9x4.9x1.27P | C7433 | 9
14 Position Header Connector 0.100" (2.54mm) Through Hole Tin | UA2,UB2 | TH-14P | C7262283 | 2
5 Position Header Connector 0.100" (2.54mm) Through Hole Tin | UC2 | Plugin,P=2.54mm | C3320579 | 1
Isolated Module DC DC Converter 2 Output 15V -15V 33mA, | U6 | SIP,19.7x6mm | C6263143 | 1
Connector Header Through Hole 10 position 0.100" (2.54mm) | P13,P14 | TH-2X5P,P=2.54mm | C7497904 | 2
Connector Header Through Hole 4 position 0.100" (2.54mm) | P15,P16 | Plugin,P=2.54mm | C3333300 | 2
Connector Header Through Hole, Right Angle 3 position 0.100" | K1 | Push-Pull,P=2.54mm | C3329401 | 1
2 Position Wire to Board Terminal Block Horizontal with Board | P1,P2,P3 | Plugin,P=3.5mm | C3818107 | 3

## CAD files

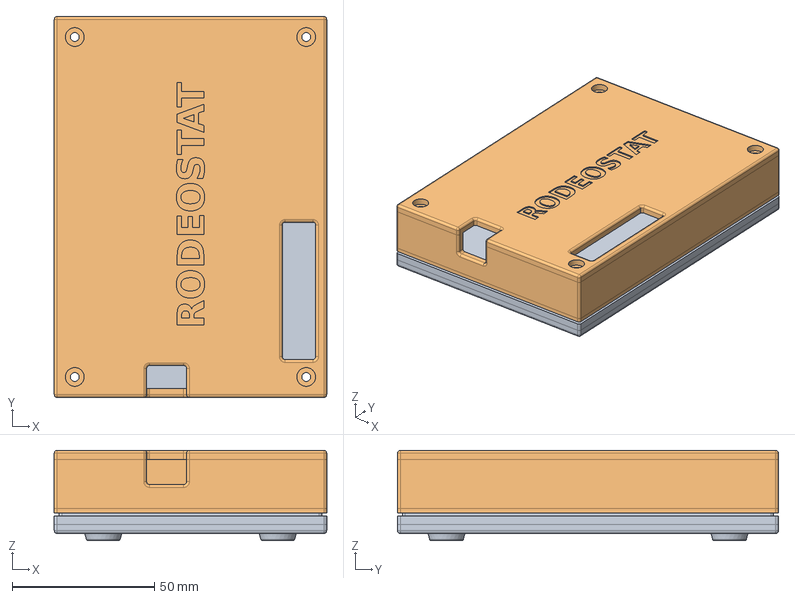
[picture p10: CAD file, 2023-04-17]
hardware/enclosures/3d_printer/rodeostat_enclosure/step/v1r3/assembly_test.FCStd
95.7 x 133.8 x 31.7 mm
enclosure_bottom_v1r31_001
enclosure_top_v1r31_001

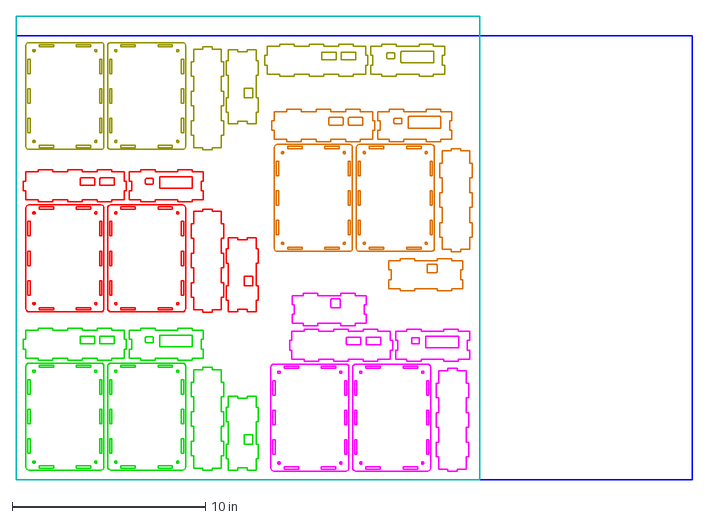
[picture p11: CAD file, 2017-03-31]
hardware/enclosures/acrylic_v0p1/lasercut/fullsheet/layout_fullsheet.dxf
35.0 x 24.0 in

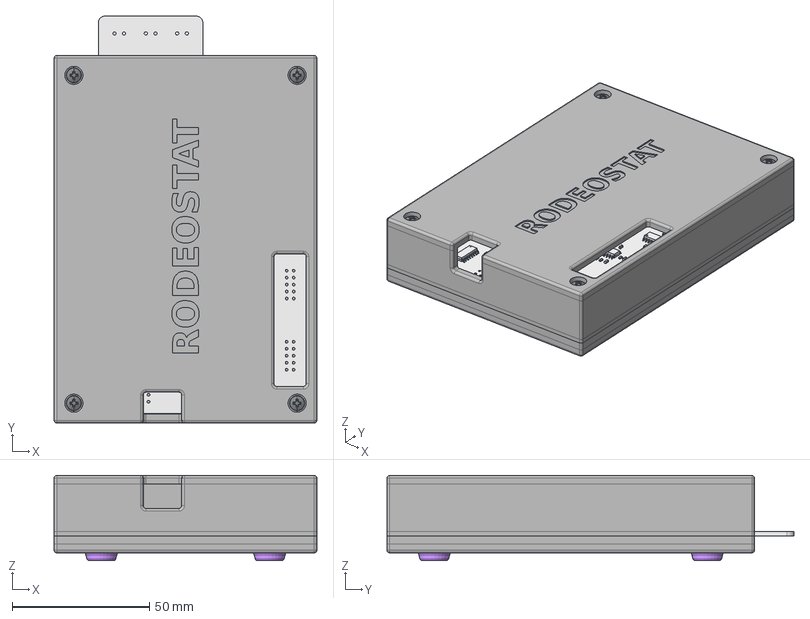
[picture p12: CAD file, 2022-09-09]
hardware/enclosures/3d_printer/rodeostat_enclosure/enclosure_assembly.FCStd
95.7 x 148.2 x 31.0 mm
enclosure_bottom
enclosure_top
rodeostat_pcb
hexnut_4-40_narrow1_001
hexnut_4-40_narrow1_002
hexnut_4-40_narrow1_003
hexnut_4-40_narrow1_004
phillips_screw_4-40_1in1_001
phillips_screw_4-40_1in1_002
phillips_screw_4-40_1in1_003
phillips_screw_4-40_1in1_004
SJxx121_001
SJxx121_002
SJxx121_003
SJxx121_004

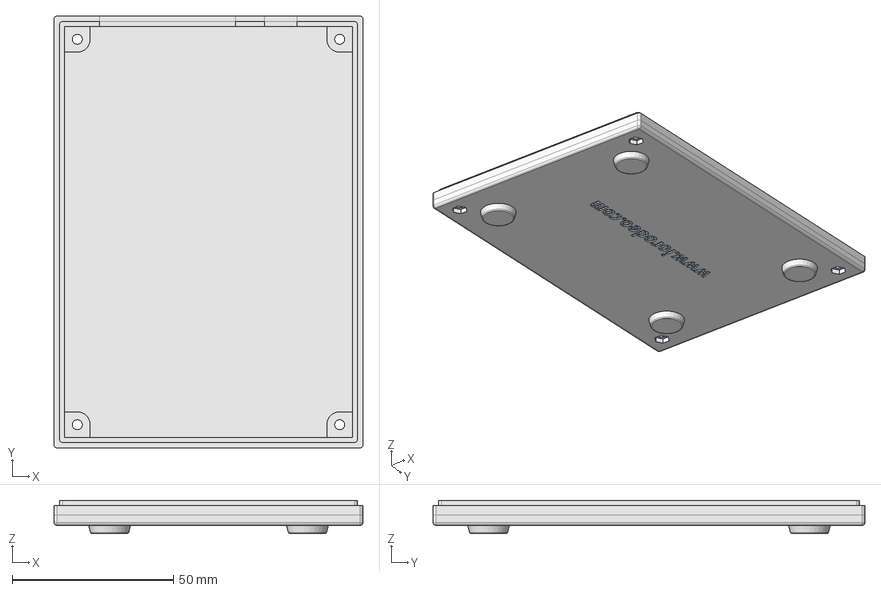
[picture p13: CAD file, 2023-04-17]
hardware/enclosures/3d_printer/rodeostat_enclosure/enclosure_bottom.FCStd
95.7 x 133.8 x 10.3 mm

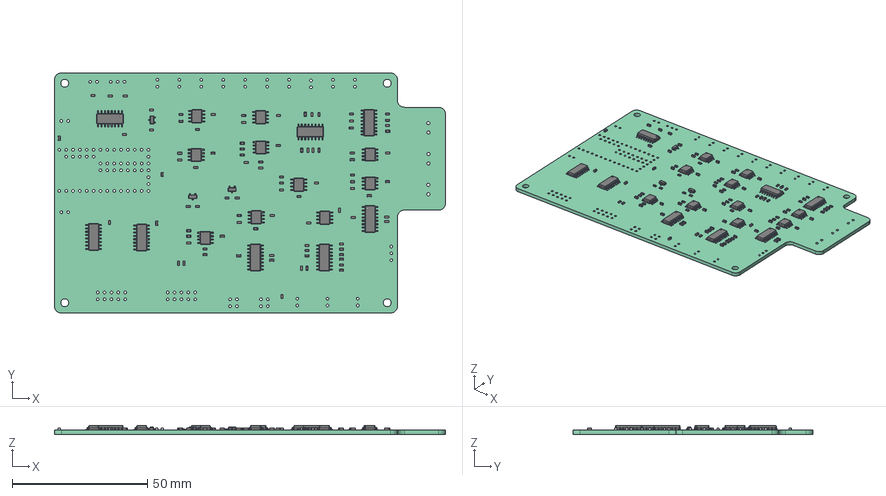
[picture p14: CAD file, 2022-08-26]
hardware/enclosures/3d_printer/rodeostat_enclosure/fittings_etc/rodeostat_pcb.step
144.8 x 88.9 x 3.35 mm
Local_CS_fac9
Pcb_fac9
PCB_Sketch_fac9
C3_C_0603_1608Metric_60208B3B x 53
U11_SOIC_8_39x49mm_P127mm_6020924B x 10
D1_SOT_23_6.0208e+95 x 3
R1_R_0603_1608Metric_60208EC1 x 38
U1_SOIC_16_39x99mm_P127mm_60209158 x 8

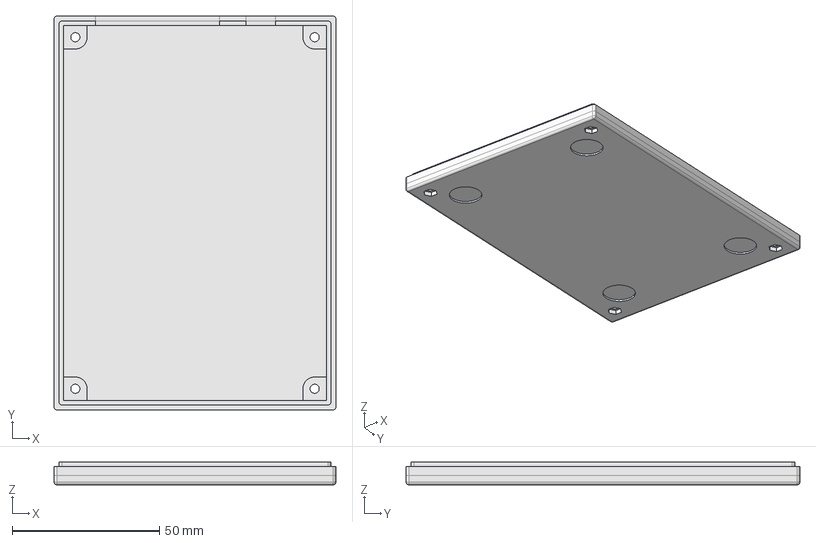
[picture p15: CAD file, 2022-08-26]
hardware/enclosures/3d_printer/rodeostat_enclosure/step/enclosure_bottom_test.step
95.7 x 133.8 x 7.80 mm

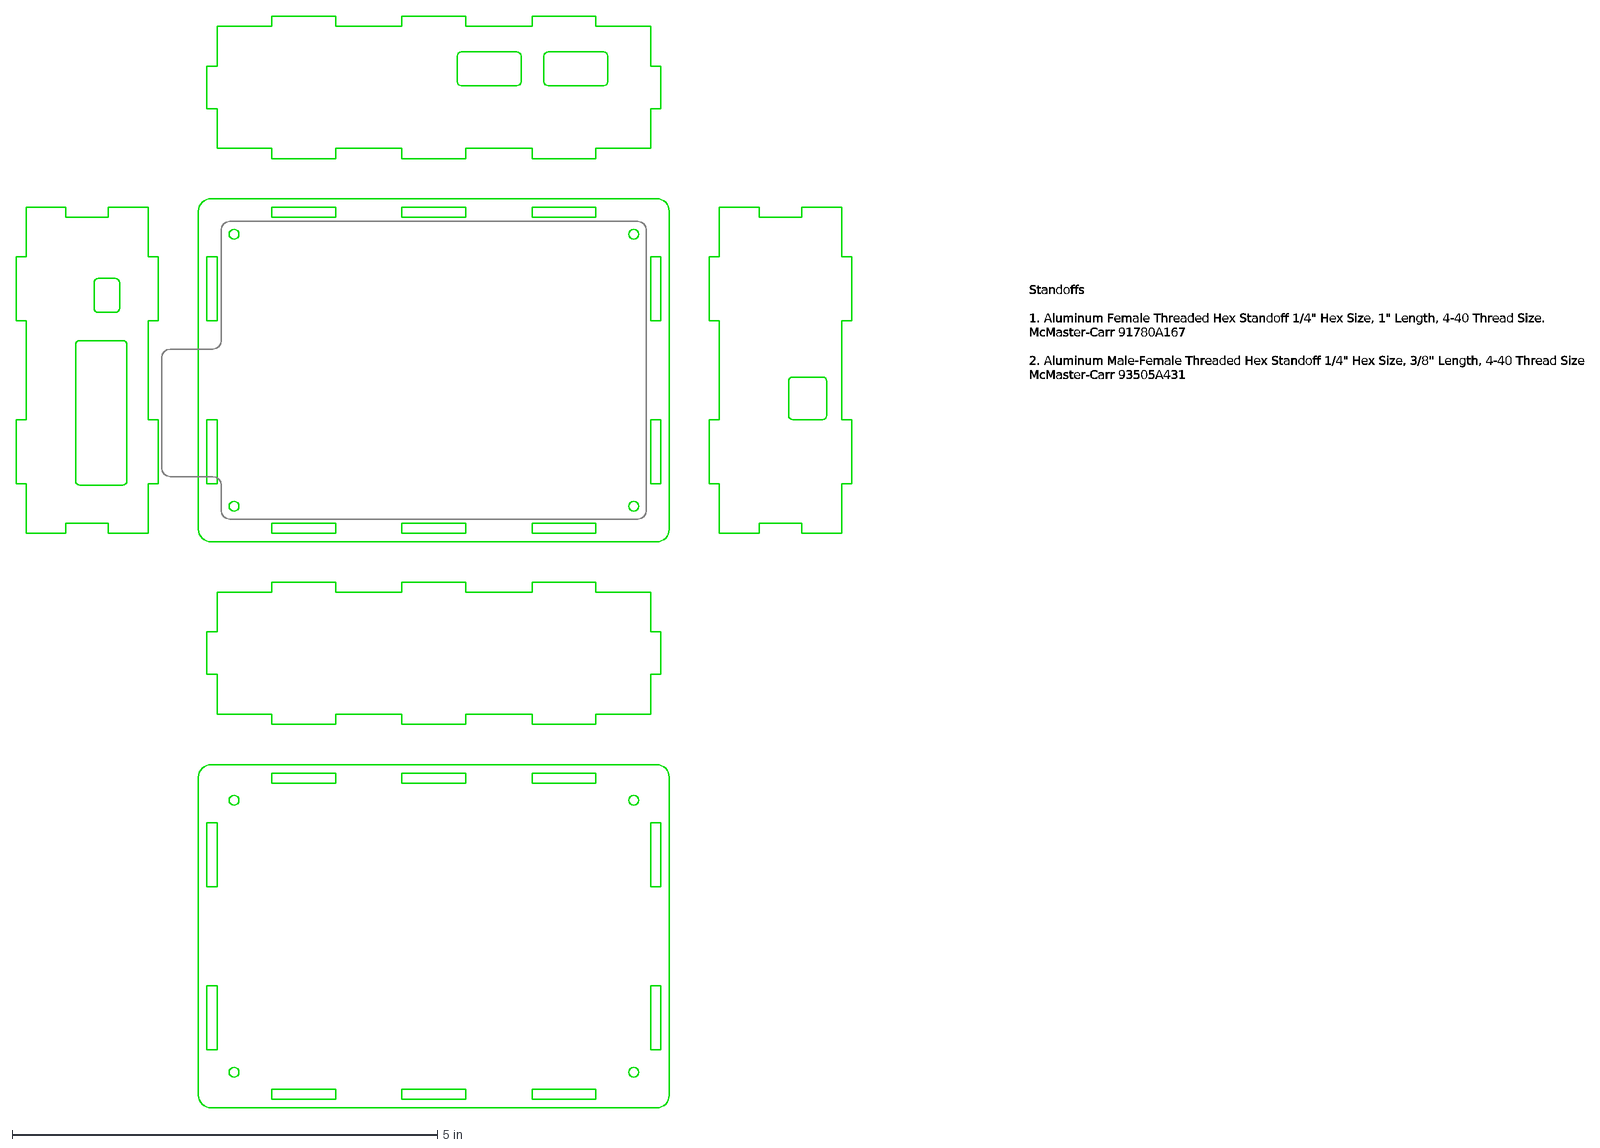
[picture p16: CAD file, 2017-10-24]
hardware/enclosures/acrylic_v0p1/enclosure.dxf
Standoffs 1. Aluminum Female Threaded Hex Standoff 1/4" Hex Size, 1" Length, 4-40 Thread Size. McMaster-Carr 91780A167 2. Aluminum Male-Female Threaded Hex Stan

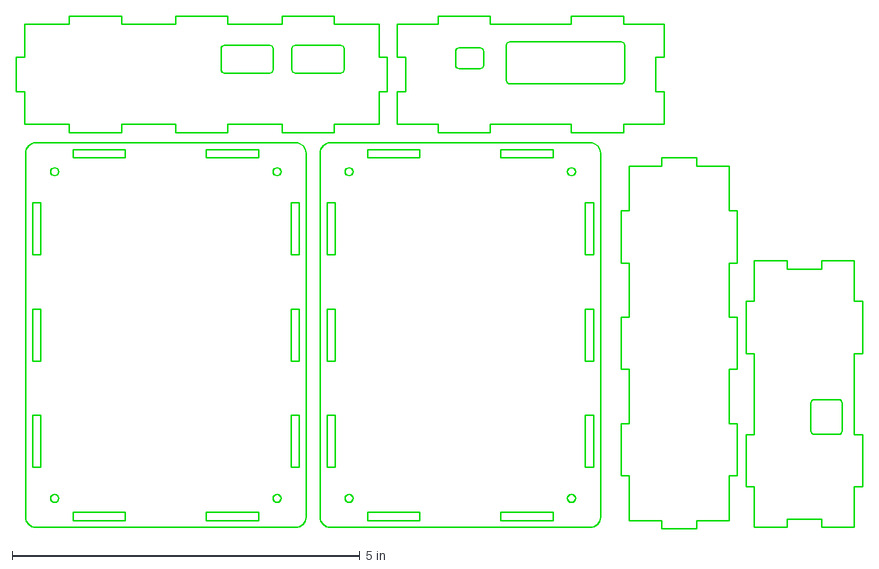
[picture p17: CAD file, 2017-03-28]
hardware/enclosures/acrylic_v0p1/lasercut/single/layout_single.dxf
12.2 x 7.37 in

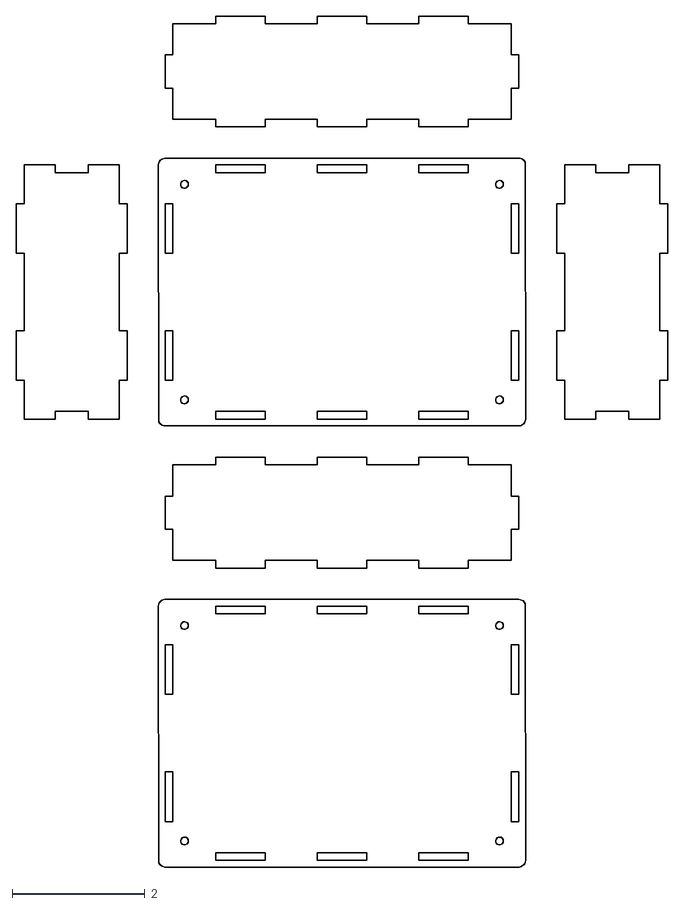
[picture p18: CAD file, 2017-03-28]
hardware/enclosures/acrylic_v0p1/template/enclosure_projection.dxf
9.83 x 12.8

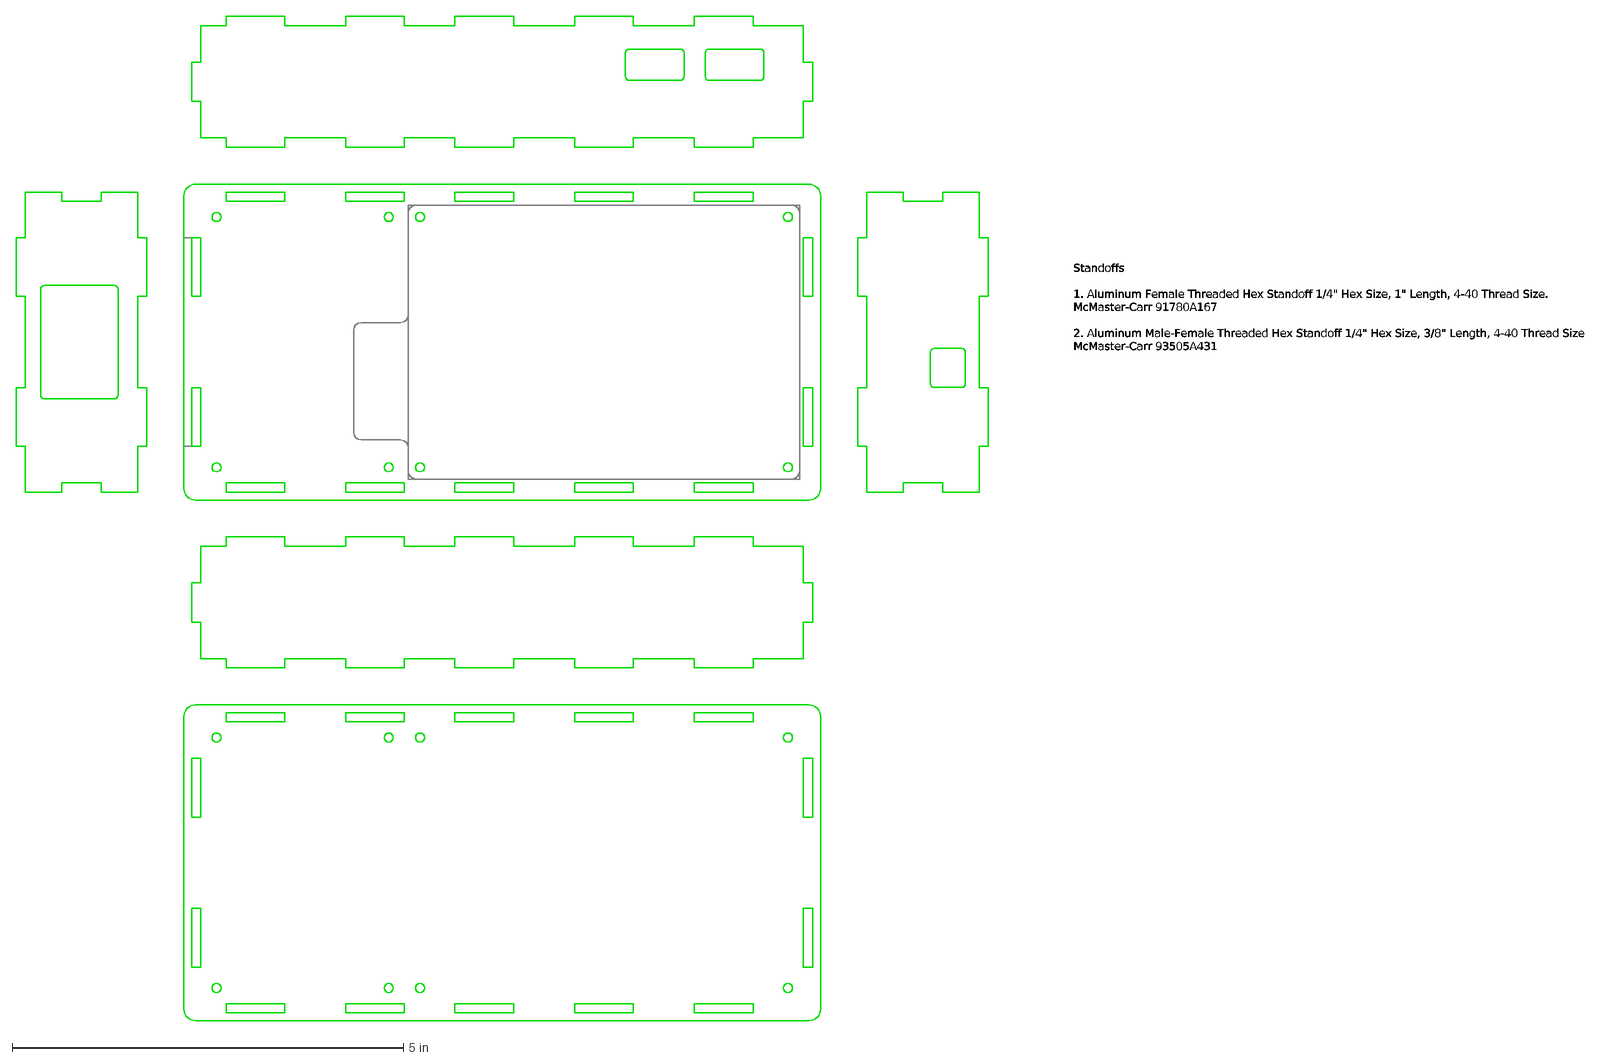
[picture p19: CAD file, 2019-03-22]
hardware/enclosures/multiplexer/enclosure.dxf
Standoffs 1. Aluminum Female Threaded Hex Standoff 1/4" Hex Size, 1" Length, 4-40 Thread Size. McMaster-Carr 91780A167 2. Aluminum Male-Female Threaded Hex Stan

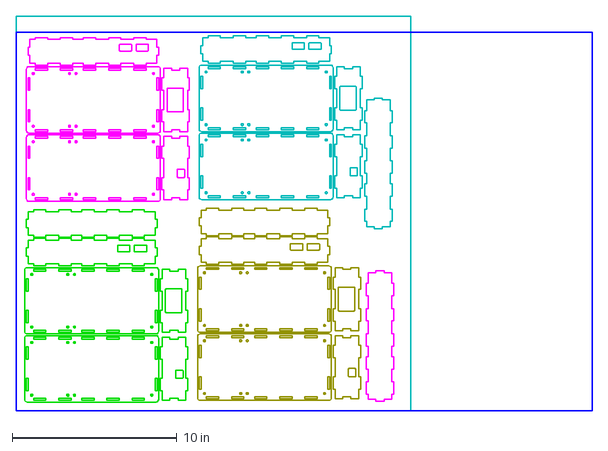
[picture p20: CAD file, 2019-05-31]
hardware/enclosures/multiplexer/lasercut/fullsheet/enclosure.dxf
35.0 x 24.0 in

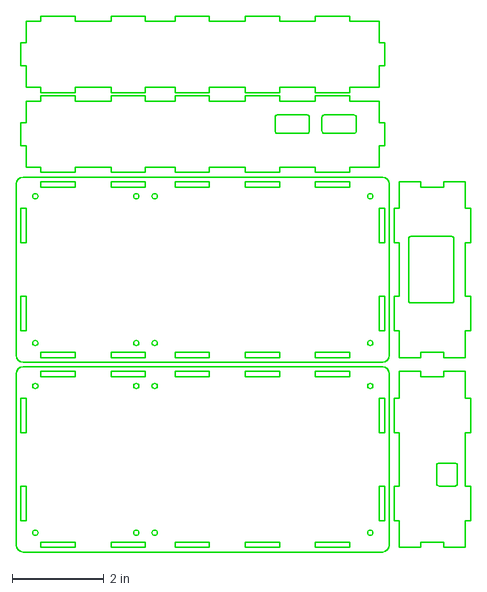
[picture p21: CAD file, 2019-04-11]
hardware/enclosures/multiplexer/lasercut/one_1st/enclosure.dxf
9.91 x 11.7 in

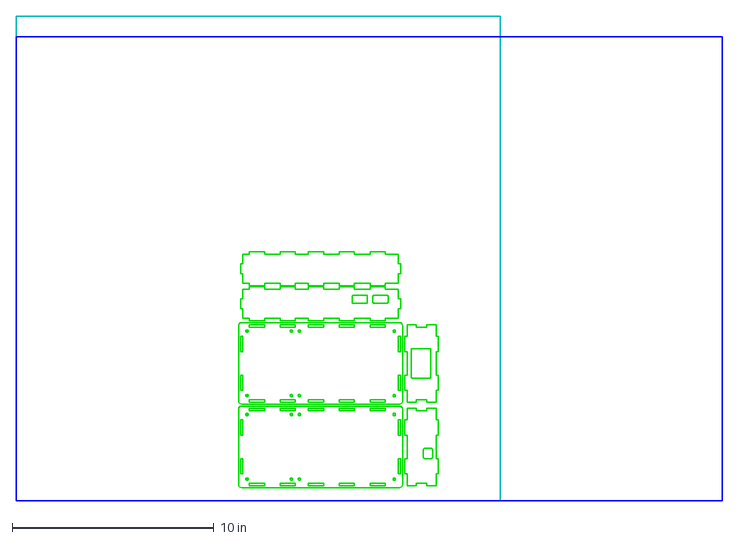
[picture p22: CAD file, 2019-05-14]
hardware/enclosures/multiplexer/lasercut/one_2nd/enclosure.dxf
35.0 x 24.0 in

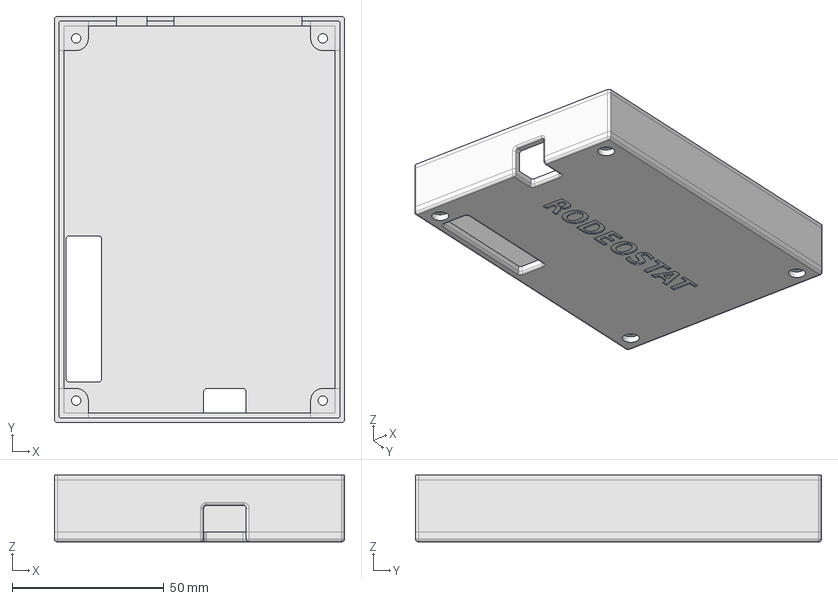
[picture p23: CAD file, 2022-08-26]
hardware/enclosures/3d_printer/rodeostat_enclosure/step/v1r1/enclosure_top_v1r1.step
95.7 x 133.8 x 22.0 mm

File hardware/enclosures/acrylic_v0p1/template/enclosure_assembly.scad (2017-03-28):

//====================================================================//
//===================== enclosure_assembly.scad ======================//
//                                                                    //
// Autogenerated using py2scad. Hand editing this file is not         //
// advisable as all modifications will be lost when the program which //
// generated this file is re-run.                                     //
//====================================================================//

$fn = 50;
translate(v=[0.00000, 0.00000, 0.77756]) {
    difference() {
        difference() {
            difference() {
                difference() {
                    difference() {
                        difference() {
                            difference() {
                                difference() {
                                    difference() {
                                        difference() {
                                            difference() {
                                                difference() {
                                                    difference() {
                                                        difference() {
                                                            union() {
                                                                cube(size=[5.33622, 3.83622, 0.11811], center=true);
                                                                translate(v=[2.66811, 0.00000, 0.00000]) {
                                                                    cube(size=[0.20000, 3.83622, 0.11811], center=true);
                                                                }
                                                                translate(v=[-2.66811, 0.00000, 0.00000]) {
                                                                    cube(size=[0.20000, 3.83622, 0.11811], center=true);
                                                                }
                                                                translate(v=[0.00000, 1.91811, 0.00000]) {
                                                                    cube(size=[5.33622, 0.20000, 0.11811], center=true);
                                                                }
                                                                translate(v=[0.00000, -1.91811, 0.00000]) {
                                                                    cube(size=[5.33622, 0.20000, 0.11811], center=true);
                                                                }
                                                                translate(v=[-2.66811, -1.91811, 0.00000]) {
                                                                    cylinder(h=0.11811,r1=0.10000,r2=0.10000,center=true);
                                                                }
                                                                translate(v=[-2.66811, 1.91811, 0.00000]) {
                                                                    cylinder(h=0.11811,r1=0.10000,r2=0.10000,center=true);
                                                                }
                                                                translate(v=[2.66811, -1.91811, 0.00000]) {
                                                                    cylinder(h=0.11811,r1=0.10000,r2=0.10000,center=true);
                                                                }
                                                                translate(v=[2.66811, 1.91811, 0.00000]) {
                                                                    cylinder(h=0.11811,r1=0.10000,r2=0.10000,center=true);
                                                                }
                                                            }
                                                            translate(v=[-1.53000, -1.85906, 0.00000]) {
                                                                cube(size=[0.75000, 0.11811, 0.23622], center=true);
                                                            }
                                                        }
                                                        translate(v=[-1.53000, 1.85906, 0.00000]) {
                                                            cube(size=[0.75000, 0.11811, 0.23622], center=true);
                                                        }
                                                    }
                                                    translate(v=[0.00000, -1.85906, 0.00000]) {
                                                        cube(size=[0.75000, 0.11811, 0.23622], center=true);
                                                    }
                                                }
                                                translate(v=[0.00000, 1.85906, 0.00000]) {
                                                    cube(size=[0.75000, 0.11811, 0.23622], center=true);
                                                }
                                            }
                                            translate(v=[1.53000, -1.85906, 0.00000]) {
                                                cube(size=[0.75000, 0.11811, 0.23622], center=true);
                                            }
                                        }
                                        translate(v=[1.53000, 1.85906, 0.00000]) {
                                            cube(size=[0.75000, 0.11811, 0.23622], center=true);
                                        }
                                    }
                                    translate(v=[-2.60906, -0.95906, 0.00000]) {
                                        cube(size=[0.11811, 0.75000, 0.23622], center=true);
                                    }
                                }
                                translate(v=[2.60906, -0.95906, 0.00000]) {
                                    cube(size=[0.11811, 0.75000, 0.23622], center=true);
                                }
                            }
                            translate(v=[-2.60906, 0.95906, 0.00000]) {
                                cube(size=[0.11811, 0.75000, 0.23622], center=true);
                            }
                        }
                        translate(v=[2.60906, 0.95906, 0.00000]) {
                            cube(size=[0.11811, 0.75000, 0.23622], center=true);
                        }
                    }
                    translate(v=[-2.37500, -1.62500, 0.00000]) {
                        cylinder(h=0.23622,r1=0.05800,r2=0.05800,center=true);
                    }
                }
                translate(v=[-2.37500, 1.62500, 0.00000]) {
                    cylinder(h=0.23622,r1=0.05800,r2=0.05800,center=true);
                }
            }
            translate(v=[2.37500, -1.62500, 0.00000]) {
                cylinder(h=0.23622,r1=0.05800,r2=0.05800,center=true);
            }
        }
        translate(v=[2.37500, 1.62500, 0.00000]) {
            cylinder(h=0.23622,r1=0.05800,r2=0.05800,center=true);
        }
    }
}
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

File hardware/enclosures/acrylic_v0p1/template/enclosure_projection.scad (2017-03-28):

//====================================================================//
//==================== enclosure_projection.scad =====================//
//                                                                    //
// Autogenerated using py2scad. Hand editing this file is not         //
// advisable as all modifications will be lost when the program which //
// generated this file is re-run.                                     //
//====================================================================//

$fn = 50;
projection(cut=true) {
    translate(v=[4.07716, 0.00000, 0.00000]) {
        rotate(a=90.00000,v=[0.00000, 0.00000, 1.00000]) {
            difference() {
                union() {
                    cube(size=[3.83622, 1.43700, 0.11811], center=true);
                    translate(v=[-0.95906, 0.71850, 0.00000]) {
                        cube(size=[0.75000, 0.23622, 0.11811], center=true);
                    }
                    translate(v=[0.95906, 0.71850, 0.00000]) {
                        cube(size=[0.75000, 0.23622, 0.11811], center=true);
                    }
                    translate(v=[-0.95906, -0.71850, 0.00000]) {
                        cube(size=[0.75000, 0.23622, 0.11811], center=true);
                    }
                    translate(v=[0.95906, -0.71850, 0.00000]) {
                        cube(size=[0.75000, 0.23622, 0.11811], center=true);
                    }
                }
                translate(v=[1.91811, 0.00000, 0.00000]) {
                    cube(size=[0.23622, 0.50000, 0.17717], center=true);
                }
                translate(v=[-1.91811, 0.00000, 0.00000]) {
                    cube(size=[0.23622, 0.50000, 0.17717], center=true);
                }
            }
        }
    }
}

projection(cut=true) {
    difference() {
        difference() {
            difference() {
                difference() {
                    difference() {
                        difference() {
                            difference() {
                                difference() {
                                    difference() {
                                        difference() {
                                            difference() {
                                                difference() {
                                                    difference() {
                                                        difference() {
                                                            union() {
                                                                cube(size=[5.33622, 3.83622, 0.11811], center=true);
                                                                translate(v=[2.66811, 0.00000, 0.00000]) {
                                                                    cube(size=[0.20000, 3.83622, 0.11811], center=true);
                                                                }
                                                                translate(v=[-2.66811, 0.00000, 0.00000]) {
                                                                    cube(size=[0.20000, 3.83622, 0.11811], center=true);
                                                                }
                                                                translate(v=[0.00000, 1.91811, 0.00000]) {
                                                                    cube(size=[5.33622, 0.20000, 0.11811], center=true);
                                                                }
                                                                translate(v=[0.00000, -1.91811, 0.00000]) {
                                                                    cube(size=[5.33622, 0.20000, 0.11811], center=true);
                                                                }
                                                                translate(v=[-2.66811, -1.91811, 0.00000]) {
                                                                    cylinder(h=0.11811,r1=0.10000,r2=0.10000,center=true);
                                                                }
                                                                translate(v=[-2.66811, 1.91811, 0.00000]) {
                                                                    cylinder(h=0.11811,r1=0.10000,r2=0.10000,center=true);
                                                                }
                                                                translate(v=[2.66811, -1.91811, 0.00000]) {
                                                                    cylinder(h=0.11811,r1=0.10000,r2=0.10000,center=true);
                                                                }
                                                                translate(v=[2.66811, 1.91811, 0.00000]) {
                                                                    cylinder(h=0.11811,r1=0.10000,r2=0.10000,center=true);
                                                                }
                                                            }
                                                            translate(v=[-1.53000, -1.85906, 0.00000]) {
                                                                cube(size=[0.75000, 0.11811, 0.23622], center=true);
                                                            }
                                                        }
                                                        translate(v=[-1.53000, 1.85906, 0.00000]) {
                                                            cube(size=[0.75000, 0.11811, 0.23622], center=true);
                                                        }
                                                    }
                                                    translate(v=[0.00000, -1.85906, 0.00000]) {
                                                        cube(size=[0.75000, 0.11811, 0.23622], center=true);
                                                    }
                                                }
                                                translate(v=[0.00000, 1.85906, 0.00000]) {
                                                    cube(size=[0.75000, 0.11811, 0.23622], center=true);
                                                }
                                            }
                                            translate(v=[1.53000, -1.85906, 0.00000]) {
                                                cube(size=[0.75000, 0.11811, 0.23622], center=true);
                                            }
                                        }
                                        translate(v=[1.53000, 1.85906, 0.00000]) {
                                            cube(size=[0.75000, 0.11811, 0.23622], center=true);
                                        }
                                    }
                                    translate(v=[-2.60906, -0.95906, 0.00000]) {
                                        cube(size=[0.11811, 0.75000, 0.23622], center=true);
                                    }
                                }
                                translate(v=[2.60906, -0.95906, 0.00000]) {
                                    cube(size=[0.11811, 0.75000, 0.23622], center=true);
                                }
                            }
                            translate(v=[-2.60906, 0.95906, 0.00000]) {
                                cube(size=[0.11811, 0.75000, 0.23622], center=true);
                            }
                        }
                        translate(v=[2.60906, 0.95906, 0.00000]) {
                            cube(size=[0.11811, 0.75000, 0.23622], center=true);
                        }
                    }
                    translate(v=[-2.37500, -1.62500, 0.00000]) {
                        cylinder(h=0.23622,r1=0.05800,r2=0.05800,center=true);
                    }
                }
                translate(v=[-2.37500, 1.62500, 0.00000]) {
                    cylinder(h=0.23622,r1=0.05800,r2=0.05800,center=true);
                }
            }
            translate(v=[2.37500, -1.62500, 0.00000]) {
                cylinder(h=0.23622,r1=0.05800,r2=0.05800,center=true);
            }
        }
        translate(v=[2.37500, 1.62500, 0.00000]) {
            cylinder(h=0.23622,r1=0.05800,r2=0.05800,center=true);
        }
    }
}
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

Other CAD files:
hardware/enclosures/3d_printer/rodeostat_enclosure/step/v1r1/enclosure_bottom_v1r1.step
hardware/enclosures/3d_printer/rodeostat_enclosure/step/v1r2/enclosure_bottom_v1r2.step
hardware/enclosures/3d_printer/rodeostat_enclosure/step/v1r3/enclosure_bottom_v1r3.step
hardware/enclosures/acrylic_v0p1/potentiostat-Edge_Cuts.dxf
hardware/enclosures/3d_printer/rodeostat_enclosure/enclosure_top.FCStd
hardware/enclosures/3d_printer/rodeostat_enclosure/fittings_etc/hexnut_4-40_narrow.step
hardware/enclosures/3d_printer/rodeostat_enclosure/fittings_etc/phillips_screw_4-40_1in.step
hardware/enclosures/3d_printer/rodeostat_enclosure/step/v1r3/enclosure_top_v1r3.step
hardware/enclosures/multiplexer/lasercut/one_1st/test_base.dxf

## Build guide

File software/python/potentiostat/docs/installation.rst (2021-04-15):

############
Installation
############

This library is tested on Python 2.7 and Python 3.x. 

********************
Installing from PyPI
********************

You can install the iorodeo-potentiostat library from `PyPi`_ using pip as follows:

.. code-block:: bash

  $ pip install iorodeo-potentiostat

If you are installing using pip then all required dependencies should
automatically be downloaded and installed when running this command.

**********************
Installing from source
**********************

An alternative installation method is to download and install from source. If
you would like to install in this manner the  source for the library can be
found in the `potentiostat shield repository`_.  After downloading a copy of
the repository you can install the software by running the following command in
the module's top level directory (software/python/potentiostat).

.. code-block:: bash

  $ python setup.py install

If your are installing from source (not with pip) then you will also need to
install the following dependencies:

* `Pyserial >= 2.6`_ 
* `Progressbar33`_ 

**********
Virtualenv
**********

If you are developing with the library it is very likely that you will want to
use `virtualenv`_ during installation. A tutorial describing how to use virtualenv
can be found here `virtualenv tutorial`_  and more detailed information can be
found in the `virtualenv documentation`_.  If you are using the library on
Windows you might want to look this additional tutorial `Python, pip and
virtuanenv on Windows`_. 

Driver (Windows Only)
=====================

On versions of windows < 10. You will need to install a driver in order to communicate with the
teensy 3.2 as a serial port. The easiest way to do this is to run the `teensyduino installer`_.

Note, this step is not required on Linux or on Mac OS.

udev rules (Linux only)
=======================
On Linux you may want to give non-root users permission to use the teensy
device. This can be done by adding the `49-teensy.rules`_ file to the
/etc/udev/rules.d directory and reloading the rules using udevadm. 

Copy to /etc/udev/rules.d as follows

.. code-block:: bash

  $ sudo cp 49-teensy.rules /etc/udev/rules.d/

Reload udev rules

.. code-block:: bash

  $ sudo udevadm control --reload-rules

**********
References
**********

.. target-notes::

.. _`PyPI`: https://pypi.python.org/pypi
.. _`potentiostat shield repository`: https://github.com/iorodeo/potentiostat/
.. _`virtualenv`: https://pypi.python.org/pypi/virtualenv
.. _`virtualenv tutorial`: http://python-guide-pt-br.readthedocs.io/en/latest/dev/virtualenvs/ 
.. _`virtualenv documentation`: https://virtualenv.pypa.io/en/stable/ 
.. _`teensyduino installer`: https://www.pjrc.com/teensy/td_download.html
.. _`49-teensy.rules`: https://www.pjrc.com/teensy/49-teensy.rules
.. _`Python, pip and virtuanenv on Windows`: http://www.tylerbutler.com/2012/05/how-to-install-python-pip-and-virtualenv-on-windows-with-powershell/
.. _`Pyserial >= 2.6`: https://pythonhosted.org/pyserial/
.. _`Progressbar33`: https://pypi.python.org/pypi/progressbar33

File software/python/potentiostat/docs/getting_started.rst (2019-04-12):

.. _getting_started_ref:

###############
Getting Started
###############

This section provides a short guide to help you begin using your Rodeostat with the 
**iorodeo-potentiostat** library.

************************
Creating a device object
************************

The first step to controlling your Rodeostat is creating a device object. In
order to do this you will need to know the name of the **port** on the computer
which is associated with the Rodeostat.  The name of this port will vary
depending on your operating system, what other devices are connected to your
computer,  etc.  On linux this port will be named something like /dev/ttyACM0,
/dev/ttyACM1, ..., etc.  On Windows it will be named something like COM1, COM2,
etc. 

A device object can be created as follows

.. code-block:: python 

  from potentiostat import Potentiostat

  pstat = Potentiostat('/dev/ttyACM0')

This will open a connection which can be used to communicate with the Rodeostat. 

.. note::

    In order to reduce repetition,  in all of the examples which follow,  we
    will assume that you have already created a Potentiostat device object,
    named pstat, using the above command.

**********************************
Getting list of voltametric tests
**********************************

A list of all of the voltammetric tests supported by the current firmware on
the Rodeostat can be obtained using the
:meth:`~potentiostat.Potentiostat.get_test_names` method.

.. code-block:: python

  test_names = pstat.get_test_names()

This method will return a list, such as that given below.

.. code-block:: python

  test_names = ['cyclic', 'sinusoid', 'constant', 'squareWave', 'linearSweep', 'chronoamp', 'multiStep']

Each string in the list is name of a voltammetric test which can be run by the
firmware on the Rodeostat.  

************************************
Getting voltammetric test parameters
************************************

The current parameter values used for a particular voltammetric test are stored
in memory on the potentiostat.  You can retrieve the current values for these
parameters from the device using the :meth:`~potentiostat.Potentiostat.get_param` method. 

For example, you can  get the current parameter values for the linearSweep test using 
the following command.

.. code-block:: python

  param = pstat.get_param('linearSweep')

This method returns a dictionary containing the all of the the parameters for
the specified test and their current values.   For example, for the  
linearSweep test result would be something like the dictionary shown below.  

.. code-block:: python

  param = {'quietTime': 0, 'quietValue': 0.0, 'finalValue': 0.5, 'startValue': -0.5, 'duration': 2000}

In the above output all time values, such as quietTime and duration, are given
in (ms) and all output voltages, such as quietValue, startValue and finalValue,
are given in (V).  For a complete description of the parameters for all
voltammetric see the :ref:`tests_ref` section of the documentation.

.. _getting_started_set_param_ref:

************************************
Setting voltammetric test parameters
************************************

The :meth:`~potentiostat.Potentiostat.set_param` method can be used to set the
parameters used for a specific voltammetric test. The parameters are stored in
RAM (voltile memory) on the Rodeostat. They will retain their value, for the
specified test,  as long as the Rodeostat has power or until changed via
another call to the :meth:`~potentiostat.Potentiostat.set_param` method.

The following example  demonstrates how to set the parameters for the *linearSweep* test.

.. code-block:: python

  param = {'quietTime': 0, 'quietValue': 0.0, 'finalValue': 0.5, 'startValue': -0.5, 'duration': 2000}

  pstat.set_param('linearSweep',param)
  
In the param dictionary above all time values, such as quietTime and duration,
are given in (ms) and all output voltages, such as quietValue, startValue and
finalValue, are given in (V).  For a complete description of the parameters for
all voltammetric see the :ref:`tests_ref` section of the documentation.

.. note::

  The parameter values for all voltammetric test are stored in volatile memory.
  Because of this, after a power cycle of the Rodeostat,  all parameters will
  revert to their default  values. 

*****************************************
Getting/setting measurement current range
*****************************************

The Rodeostat has four programmable current measurement ranges. The
exact values for the avialable ranges is determined by the hardware variant of
the device you are using. The library will automatically
detect the hardware variant of the device for you and you can retrieve  the
current ranges available on your device using the
:meth:`~potentiostat.Potentiostat.get_all_curr_range` method. 

.. code-block:: python

  curr_range_list = pstat.get_all_curr_range()

This will return a list of strings representing the available current ranges
such as that given below.

.. code-block:: python

  curr_range_list = ['1uA', '10uA', '100uA', '1000uA']

To get the current measurement range which your device is currently using 
you can use the the :meth:`~potentiostat.Potentiostat.get_curr_range` method. 

.. code-block:: python

  curr_range = pstat.get_curr_range()

This will return a string representation of the current measurement range. 

.. code-block:: python

  curr_range = '10uA'

In order to set the desired current measurement range on your device you can
use the :meth:`~potentiostat.Potentiostat.set_curr_range` method. For example,
to change the current range to 100uA you could do the following.

.. code-block:: python

  pstat.set_curr_range('100uA')

.. note::

    All current ranges supported by the device are bipolar and  measure both
    positive and negative currents. For example, the 10uA current
    range can measure current in the range -10uA to +10uA. 

***************************
Getting/setting sample rate
***************************
When running a test the device returns measurements at a specified rate
(samples/sec) for the duration of the test.  You can use the
:meth:`~potentiostat.Potentiostat.get_sample_rate` method to retrieve the
current value of sample rate used for measurements. 

.. code-block:: python

  sample_rate = pstat.get_sample_rate()

This method will return the current sample rate, in samples/sec, as floating
point number.

If you want to change the sample rate used for measurements you can use the
:meth:`~potentiostat.Potentiostat.set_sample_rate` method. For example, to set the
current sample rate to 50 samples/sec you would do the following.

.. code-block:: python

  pstat.set_sample_rate(50.0)

As an alternative you can also set/get the time between samples or sample
period.  The sample period will alwasy be equal to 1/sample_rate.  The
:meth:`~potentiostat.Potentiostat.get_sample_period` method returns the
sample_period in seconds.

.. code-block:: python

   sample_period = pstat.get_sample_period()

Similarly, the :meth:`~potentiostat.Potentiostat.set_sample_period` method sets
the sample period (given in seconds). 

.. code-block:: python

   pstat.set_sample_period(0.02)

***************************
Running  voltammetric tests
***************************

Voltammetric tests can be run using the
:meth:`~potentiostat.Potentiostat.run_test` method. For example, in order to
run the cyclic voltammetry test you could do the following. 

.. code-block:: python

   t, volt, curr = pstat.run_test('cyclic')

This method will return lists which contain the measurement times (s), voltages (V) and
currents (uA) respectively.  The test will be run with the parameter values
set in the potentiostat's memory for the specified test. 

This method takes several optional keyword arguments. For example, if you want
to save the data to a file while the test proceeds you can specify the file name 
using the *filename* keyword. 

.. code-block:: python

   t, volt, curr = pstat.run_test('cyclic', filename='data.txt')

The *param* keyword argument lets you specify the value of the parameters to
use for the test. In this case the parameter values will first be set to the
values specified and then the Rodeostat will run the test.

.. code-block:: python

    my_param = {
            'quietValue' : 0.0,
            'quietTime'  : 1000,
            'amplitude'  : 2.0,
            'offset'     : 0.0,
            'period'     : 1000,
            'numCycles'  : 5,
            'shift'      : 0.0,
            }

   t, volt, curr = pstat.run_test('cyclic', param=my_param)

For more complete documentation on the
:meth:`~potentiostat.Potentiostat.run_test` method see the :ref:`api_ref`
section.  For a more complete description of the various voltammetric tests see
:ref:`tests_ref` section. 

.. note::

  Note, when running tests with the :meth:`~potentiostat.Potentiostat.run_test`
  method the output voltage range is automatically be selected by the firmware
  prior to running the test. Thus you do not need to specifically select the
  output voltage range before using this method. 

****************************
Setting output voltage range
****************************

Under certain circumstances, such as when using manual/direct control rather
than a pre-programmed test proceedure,  you may want set the output voltage
range of the Rodeostat directly. This can be done using the
:meth:`~potentiostat.Potentiostat.set_volt_range` method.

You can retrieve the list of available output voltage ranges supported by the
device using the :meth:`~potentiostat.Potentiostat.get_all_volt_range` method.

.. code-block:: python

  volt_range_list = pstat.get_all_volt_range()

This will return a list of strings representing the available voltage ranges like that below

.. code-block:: python

  volt_range_list = ['1V', '2V', '5V', '10V']

To set set the voltage range you can use the
:meth:`~potentiostat.Potentiostat.set_volt_range` method.  For example, to set
the voltage range to '2V' you would do the following. 

.. code-block:: python

    pstat.set_volt_range('2V')

.. note::

   The output voltage ranges supported by the potentiostat are bipolar i.e., they
   including both negative and positive voltages. For example the 2V voltage
   range allows output voltages from -2V to +2V. 

***********************
Manual/direct operation
***********************

When operating the potentiostat manually you set the output voltage directly
using the :meth:`~potentiostat.Potentiostat.set_volt` method rather than using
a pre-programmed voltammetric test. For example, the following command will set
the output voltage (potential between working and reference electrodes) to 0.75V

.. code-block:: python

  pstat.set_volt(0.75)

The potentiostat will maintain this output voltage  until you change it with
another call to :meth:`~potentiostat.Potentiostat.set_volt` or you run a test
with the :meth:`~potentiostat.Potentiostat.run_test` method.  In a similar
manner, during manual operation,  you can use the
:meth:`~potentiostat.Potentiostat.get_curr` method to get a single immediate
measurement of the current  

.. code-block:: python

  curr = pstat.get_curr()

The current is returned as floating point number with units of (uA).   

Using these two methods described above,
:meth:`~potentiostat.Potentiostat.set_volt` and
:meth:`~potentiostat.Potentiostat.get_curr`, you can easily program simple time
varying voltametric tests - provided that the timing requirements are not too
demanding.  For a more detialed example demonstrating manual control see the
:ref:`examples_ref` section.

.. note::

    Prior to operating the potentiostat manually/directly you will want to set
    the output voltage range such that it spans all voltages will will occur
    during your test.  Setting the output voltage outside of the range will
    result in clipping of the output to the maximum/minimum value in the
    voltage range.  Also, changing the output voltage range during a test is
    inadvisable as it may cause glitch in the output voltage as the Rodeostat
    switches from one range to the other. 

************************************
Setting device identification number
************************************

An identifying number can be assigned to the Rodeostat using the
:meth:`~potentiostat.Potentiostat.set_device_id` method. For example, the
following command will set the device identification number to 5. 

.. code-block:: python

  pstat.set_device_id(5)

This idenitfying number is stored in non-volatile memory and thus will maintain
its value even when the device loses power.  This is useful in situations where
a program controlling more than one Rodeostat at a given time and needs a
simple mechanism to disambiguate them. 

The device identification number can be read using the
:meth:`~potentiostat.Potentiostat.get_device_id` method as shown below.

.. code-block:: python

  device_id = pstat.get_device_id()

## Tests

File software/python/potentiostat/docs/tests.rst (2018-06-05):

.. _tests_ref:

#################
Voltametric Tests 
#################

In this section we describe pre-programmed tests defined the potentiostat
shield's firmware. 

******************
Cyclic voltammetry 
******************

In cyclic voltammetry current is measured while the potential (voltage) between
the working and reference electrode is ramped up and down cyclically in piecewise
linear fashion - in a triangle waveform - for a number of cycles.  This triangle
waveform can be specified by the *amplitude*, *offset*, *period* and (phase)
*shift* in a manner similar to a sine wave.  Prior to beginning the triangle
waveform output, the  test procedure waits for a (optional) quiet period during
which the voltage is held as a user specified value. The quiet period is
defined by the *quietTime* and *quietValue* parameters.  Immediately following
the end of the quiet period the triangle waveform output begins.  The seven
parameters used to define the cyclic voltammetry test are test are summarized
in the table below.

================= ========================================= =========== ========== 
 parameter         description                               units       type     
================= ========================================= =========== ========== 
  quietValue       output value during the quiet period         V         float    
  quietTime        duration of quiet period                     ms        integer   
  amplitude        peak amplitude of triangle waveform          V         float    
  offset           offset of triangle waveform from zero        V         float    
  period           period of triangle waveform                  ms        integer  
  numCycles        number of cycles to perform                  NA        integer  
  shift            unitless phase shift for waveform            NA        float    
================= ========================================= =========== ========== 

The parameters can be set in the Rodeostat's firmware using the
:meth:`~potentiostat.Potentiostat.set_param` method and are passed as a
dictionary.  An example dictionary containing the parameters for the cyclic
voltammetry is shown below.

.. code-block:: python 

   {
        'quietValue' : -0.1,   # quiet period voltage (V) 
        'quietTime'  : 1000,   # quiet period duration (ms)
        'amplitude'  :  0.6,   # waveform peak amplitude (V) 
        'offset'     :  0.5,   # waveform offset (V)
        'period'     : 2000,   # waveform period (ms)
        'numCycles'  :    2,   # number of cycles
        'shift'      :  0.0,   # unitless phase shift
    }

The following figure illustrates the output voltage of the potentiostat with
these parameters. 

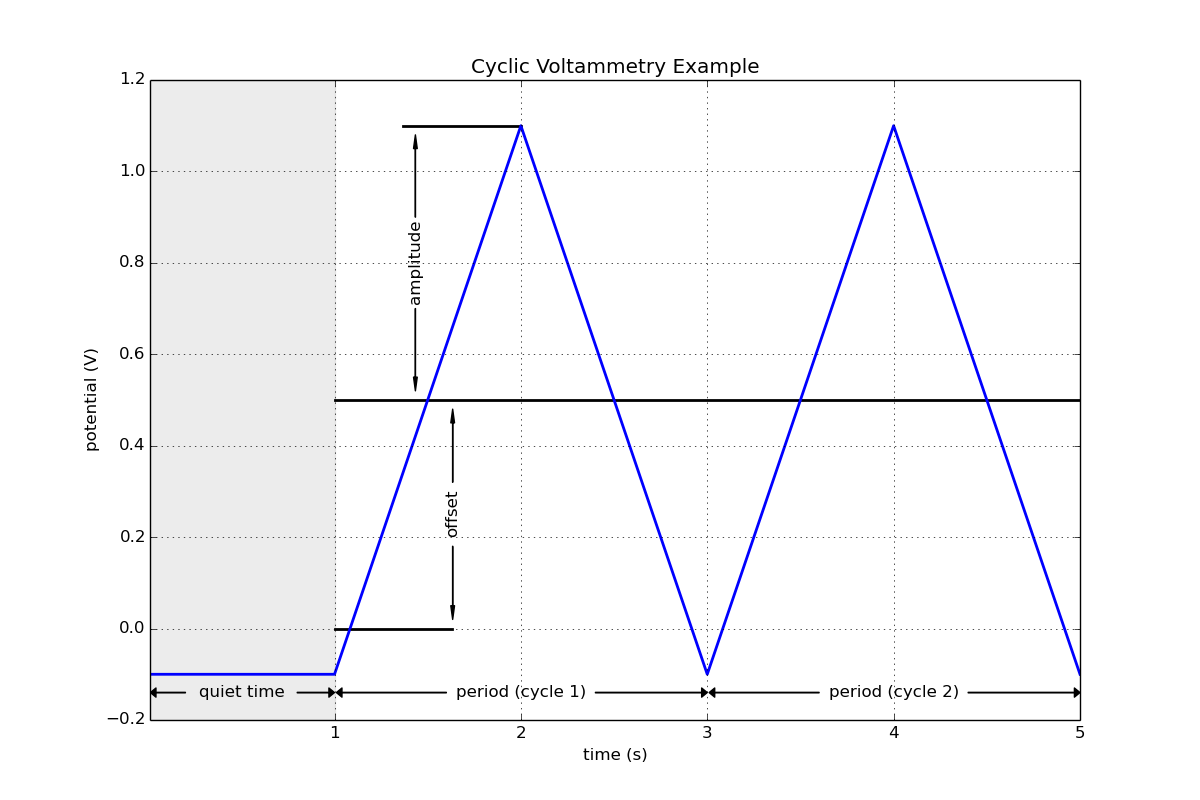
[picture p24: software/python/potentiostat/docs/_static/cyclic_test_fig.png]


When the *shift* parameter is zero the triangle waveform output for the cyclic
voltammetry test  will start at the minimum value.  This behaviour can be
changed by entering a value for the *shift* parameter in the range [0,1].  The
periodic triangle waveform will then be shifted forward (in time) by and amount
equal to *shift x period*. Thus a shift value of 1/4 would shift the triangle
waveform a quarter of a cycle forward, a shift value of 1/2 would shift the
triangle waveform a half a cycle forward, etc. An example demonstrating the effect
of the shift parameter is shown below.  

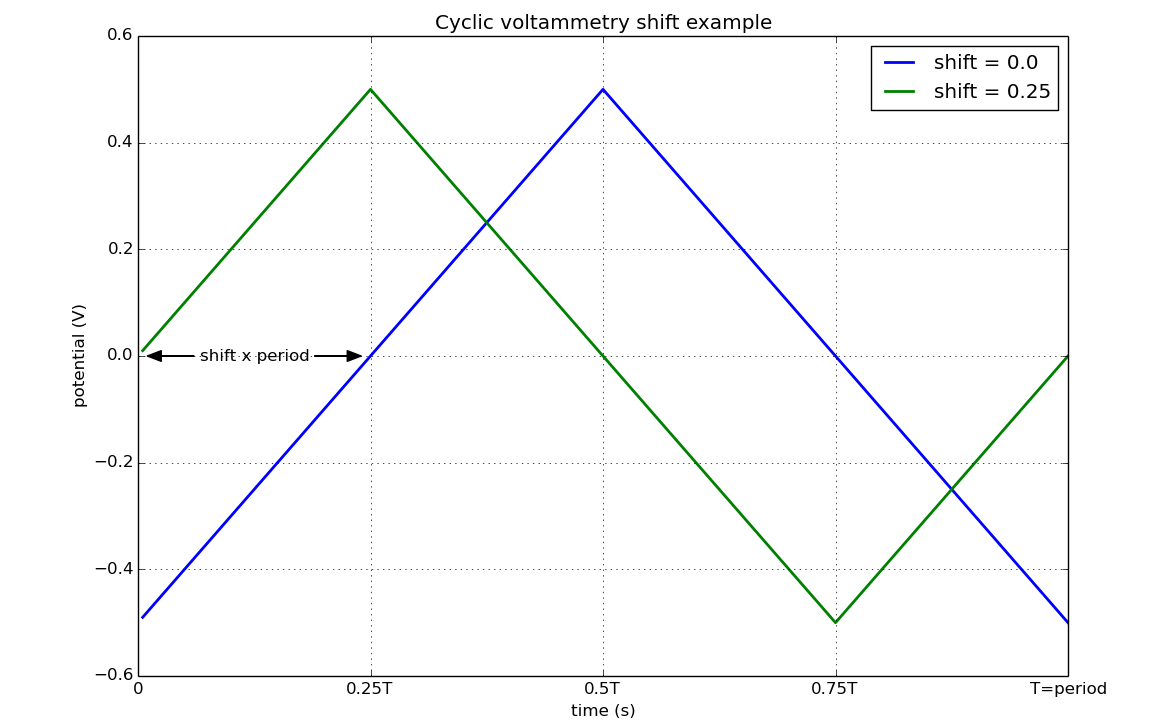
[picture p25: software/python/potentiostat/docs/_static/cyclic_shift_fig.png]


.. note::

    Sometimes the output waveform for cyclic voltammetry specified using the *scan
    rate* (V/s) and the *maximum/minimum voltage* values in the waveform. The
    relationship between these values and the *amplitude*, *offset* and *period* as are
    as follows:
    
    * scan rate = 4 x amplitude/period
    * maximum voltage = offset + amplitude
    * minimum voltage = offset - amplitude

    or alternatively

    * amplitude = 0.5 x ( (maximum voltage) - (minimum voltage) )
    * offset    = 0.5 x ( (maximum voltage) + (minimum voltage) )
    * period    = 4 x amplitude / (scan rate)

    where period has units of (s) and scan rate has units of (V/s)

More information on cyclic voltammetry can be found here `https://en.wikipedia.org/wiki/Cyclic_voltammetry`_

************************
Linear sweep voltammetry
************************

In linear sweep voltammetry current is measured while the potential between the
working and reference electrode sweeps linearly over a some range.  The range
is specified by a starting value, *startValue*, a final value, *finalValue*,
and a *duration*.  Prior to beginning the linear sweep, the test
procedure waits for a (optional) quiet period during which the voltage is held as a user
specified value.  The quiet period is specified by the quietTime and quietValue
parameters. The five parameters used to define the linear sweep voltammetry
test are test are summarized in the table below.

================= ========================================= =========== ========== 
 parameter         description                               units       type     
================= ========================================= =========== ========== 
  quietValue       output value during the quiet period         V         float    
  quietTime        duration of quiet period                     ms        integer   
  startValue       linear sweep starting value                  V         float
  finalValue       linear sweep final value                     V         float
  duration         linear sweep duration                        ms        integer
================= ========================================= =========== ========== 

The parameters can be set in the Rodeostat's firmware using the
:meth:`~potentiostat.Potentiostat.set_param` method and are passed as a
dictionary.  An example dictionary containing the five parameters for the
linear sweep voltammetry is shown below. 

.. code-block:: python 

    { 
        'quietTime'  : 2000,   # quiet period voltage (V) 
        'quietValue' :  0.0,   # quiet period duration (ms)
        'startValue' : -0.8,   # linear sweep starting value (V)
        'finalValue' :  1.2,   # linear sweep final value (V)
        'duration'   : 8000,   # linear sweep duration (ms)
    }

The following figure illustrates the output voltage of the potentiostat with
these parameters. 

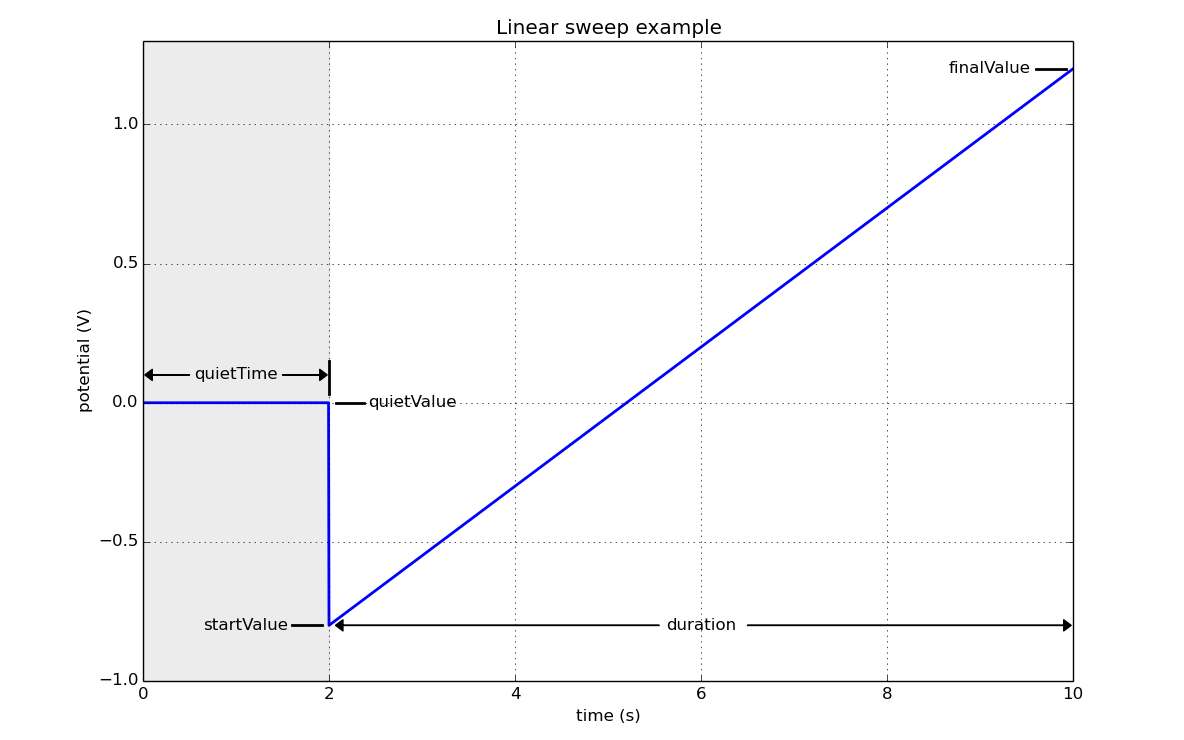
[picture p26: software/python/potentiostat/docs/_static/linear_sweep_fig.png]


.. note::

    The *scan rate* (V/s) can be found from the *startValue*, *finalValue* and *duration* 
    as follows:

    * scan rate = abs(finalValue - startValue)/duration

    where duration has units of (s). 

Additional information on linear sweep voltammetry can be found here 
`https://en.wikipedia.org/wiki/Linear_sweep_voltammetry`_

*****************
Constant voltage
*****************

The constant voltage test measures the current while the potential between the
working and reference electrode is held constant.  Like the other tests the
constant voltage test includes an optional quiet period where the output
voltage is held and constant value (quietValue) for a fixed duration
(quietTime) prior to the start of the test.  The four parameters which specify the 
voltage output for the constant voltage test are summarized in the table below.

================= ========================================= =========== ========== 
 parameter         description                               units       type     
================= ========================================= =========== ========== 
  quietValue       output value during the quiet period         V         float    
  quietTime        duration of quiet period                     ms        integer   
  value            output value during the test period          V         float
  duration         duration of the test period                  ms        integer
================= ========================================= =========== ========== 

The parameters can be set in the Rodeostat's firmware using the
:meth:`~potentiostat.Potentiostat.set_param` method and are passed as a
dictionary.  An example dictionary containing the four parameters for the
constant voltage test is shown below. 

.. code-block:: python 

    {
        'quietValue' : 0.0,
        'quietTime'  : 2000,
        'value'      : 0.7,
        'duration'   : 8000,
    }

The following figure illustrates the output voltage of the potentiostat with
these parameters. 

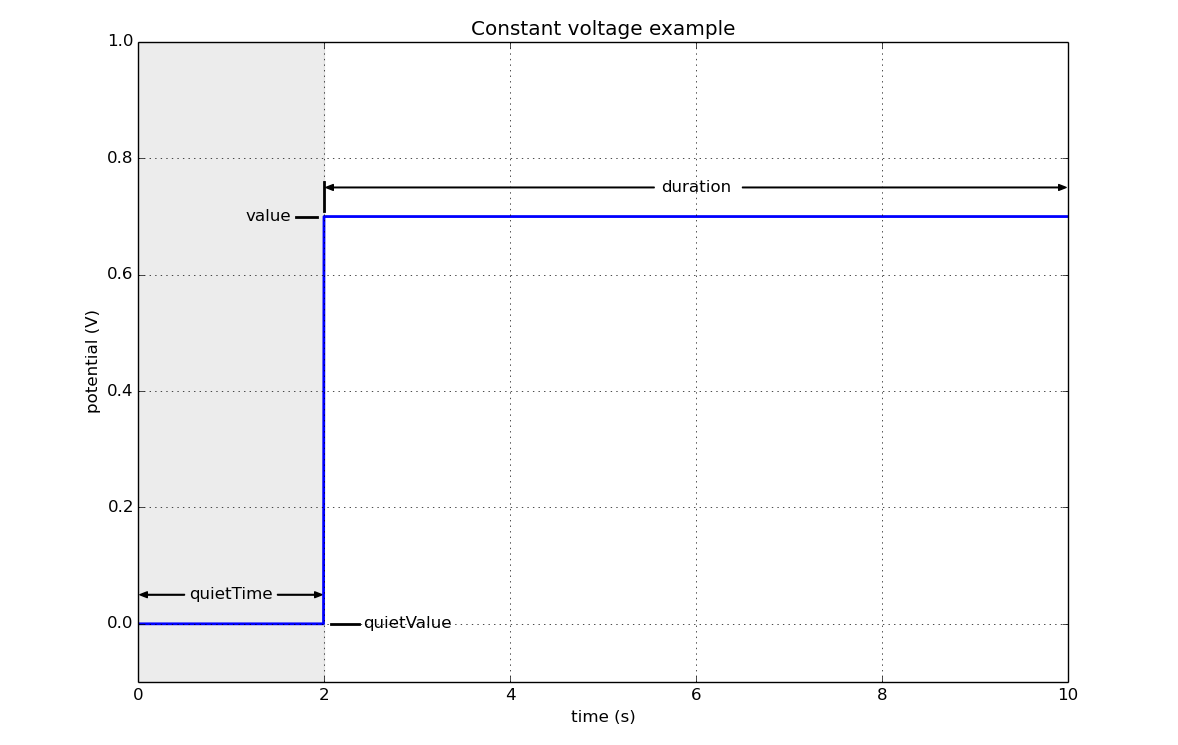
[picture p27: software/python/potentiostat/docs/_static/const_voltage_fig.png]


**********************
Sinusoidal voltammetry
**********************

================= =========================================== =========== ========== 
 parameter         description                                  units       type     
================= =========================================== =========== ========== 
  quietValue       output value during the quiet period           V         float    
  quietTime        duration of quiet period                       ms        integer   
  amplitude        peak amplitude of sinusoid waveform            V         float    
  offset           offset of sinusoid waveform from zero          V         float    
  period           period of sinusoid waveform                    ms        integer  
  numCycles        number of cycles to perform                    NA        integer  
  shift            unitless phase shift for waveform              NA        float    
================= =========================================== =========== ========== 

|

.. code-block:: python 

    {
        'quietValue' : 0.0,
        'quietTime'  : 0,
        'amplitude'  : 2.0,
        'offset'     : 0.0,
        'period'     : 2000,
        'numCycles'  : 3,
        'shift'      : 0.0,
    }

************************
Square wave voltammetry
************************

================= =========================================== =========== ========== 
 parameter         description                                  units       type     
================= =========================================== =========== ========== 
  quietValue       output value during the quiet period           V         float    
  quietTime        duration of quiet period                       ms        integer   
  amplitude        amplitude of square wave                       V         float    
  startValue       start voltage for staircase                    V         float
  finalValue       final voltage for staircase                    V         float
  stepValue        step voltage for stair case                    V         float
  window           [0,1] value size of averaging window           NA        float
================= =========================================== =========== ========== 

|

* The output waveform is the sum of a staircase and a square wave. 
* The period of the square wave is 1.0/sample_rate.
* The window parameter, a unitless number in [0,1],  sets the size of the averaging window used for sampling at the end of each half cycle. The value specifies the fraction of the half cycle used - starting from the end.  

|

.. code-block:: python

    {
        'quietValue' : -0.6, 
        'qietTime'   : 1000, 
        'startValue' : -0.6
        'finalValue' : 0.4, 
        'stepValue'  : 0.005, 
        'amplitde'   : 0.05, 
        'window'     : 0.2, 
    }

*****************
Chronoamperometry
*****************

================= ================================================= =============== ====================== 
 parameter         description                                         units           type     
================= ================================================= =============== ====================== 
  quietValue       output value during the quiet period                  V             float    
  quietTime        duration of quiet period                              ms            integer   
  step             list (len=2) of (duration,value) tuples             (ms, V)         (integer, float)
================= ================================================= =============== ====================== 

|

.. code-block:: python 

    {
        'quietValue' : 0.0,
        'quietTime'  : 1000,
        'step'       : [(1000,-0.25), (1000,0.5)],
    }

*********************
Multistep voltammetry
*********************

================= ================================================= =============== ====================== 
 parameter         description                                         units           type     
================= ================================================= =============== ====================== 
  quietValue       output value during the quiet period                  V             float    
  quietTime        duration of quiet period                              ms            integer   
  step             list (len=<50) of (duration,value) tuples             (ms, V)      (integer, float)
================= ================================================= =============== ====================== 

|

.. code-block:: python 

    {
        'quietValue' : 0.0,
        'quietTime'  : 1000,
        'step'       : [(1000,-0.5), (1000,-0.2), (1000,-0.3), (1000,-0.0), (1000,-0.1), (1000,0.3), (1000,0.2), (1000, 0.5)],
    }

**********************
Squarewave voltammetry
**********************

================= ================================================= =============== ====================== 
 parameter         description                                         units           type     
================= ================================================= =============== ====================== 
  quietValue       output value during the quiet period                  V             float    
  quietTime        duration of quiet period                              ms            integer   
  amplitude        amplitude of the squarewave                           V             float
  startValue       starting value of linear sweep                        V             float 
  finalValue       final value of linear sweep                           V             float
  stepValue        step in voltage for each cycle                        V             float
  window           fraction of half cycle used for sample                NA            float 
================= ================================================= =============== ====================== 

|

.. code-block:: python 

    {
        'quietValue' : -0.4,
        'quietTime'  :  500,
        'amplitude'  :  0.05,
        'startValue' : -0.4,
        'finalValue' :  0.2,
        'stepValue'  :  0.005,
        'window'     :  0.2,
    }

**********
References
**********

.. target-notes::

.. _`https://en.wikipedia.org/wiki/Cyclic_voltammetry`: https://en.wikipedia.org/wiki/Cyclic_voltammetry 
.. _`https://en.wikipedia.org/wiki/Linear_sweep_voltammetry`: https://en.wikipedia.org/wiki/Linear_sweep_voltammetry

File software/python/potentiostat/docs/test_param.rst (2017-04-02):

.. _test_param_ref:

#################
Voltametric Tests 
#################

******************
Cyclic voltammetry 
******************

**********************
Sinusoidal voltammetry
**********************

************************
Linear sweep voltammetry
************************

*****************
Constant voltage
*****************

*****************
Chronoamperometry
*****************

*********************
Multistep voltammetry
*********************

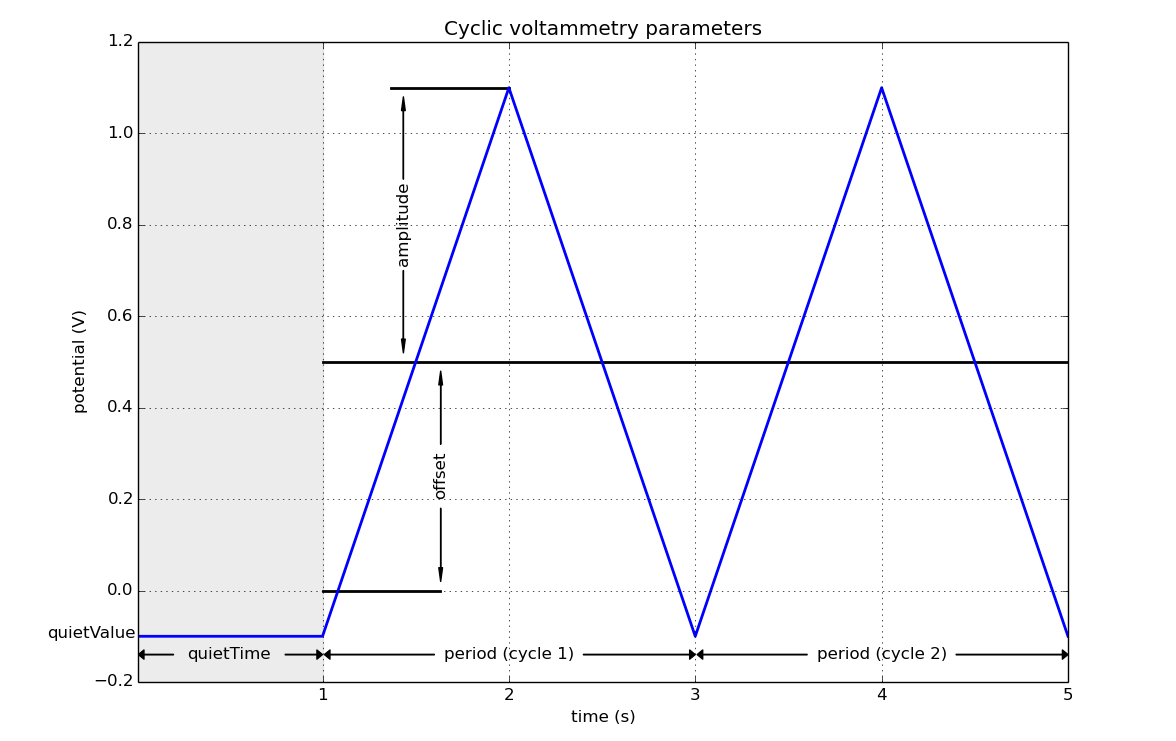
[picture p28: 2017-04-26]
software/python/potentiostat/docs/_figure_scripts/cyclic_test_fig/cyclic_test_fig.png

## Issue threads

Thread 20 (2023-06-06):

### ISSUE TITLE
Doubt about the Teensy

### ISSUE THREAD

**Issue by antonio-emilio** [iorodeo/potentiostat#20]
Hi! 
First of all, I woul'd like to congrat all contributors of the project. I woul'd like to ask if anyone see's any problem of changing the microcontroller to a ESP32... I'm having some dificculties in finding the teensy module here in Brazil.

**Comment by iorodeo** [comment]
It might be possible to use the ESP32. However, I think the ESP32 has only an 8-bit DAC which would limit the resolution of the output voltages pretty severely (just 256 values).  Also, there is a known nonlinearity in the analog inputs -  described here https://www.esp32.com/viewtopic.php?t=2881    I think it is possible to calibrate this out to some extent, but only some of the full range is available. 

We do have a new version of the Rodeostat available now https://iorodeo.com/products/rodeostat  which uses the Adafruit Itsy Bitsy M4 Express https://www.adafruit.com/product/3800     This version has pretty much same capability as the Teensy 3.2 version. The one exception being it won't work with the multiplexer expansion kit as the Itsy Bitsy M4 Express doesn't have enough IO to interface the multiplexer.  Note, you can  just put an Itsy Bitsy on the Teensy version of the Rodeostat as there are a few differences - e.g.  the pinout, etc.    However, the analog design of the potentiostat is almost exactly the same.   In addition we also have a higher current version of the Itsy Bitsy M4 Rodeostat with +/- 10, 100, 1000, and 10,000uA current ranges which will be available soon.

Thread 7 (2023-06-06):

### ISSUE TITLE
More of a question: constant current mode?

### ISSUE THREAD

**Issue by dansteingart** [iorodeo/potentiostat#7]
Awesome project. Does the standard firmware and/or standard rodeostat hardware also support galvanostatic/constant current modes?

**Comment by iorodeo** [comment]
Not currently.   If it doesn't need to be too fast then it might be possible to do this is software using manual/direct mode with the Python API http://stuff.iorodeo.com/docs/potentiostat/getting_started.html#manual-direct-operation    You could write a feedback control loop which measures the current and adjusts the output voltage to keep it constant using the get_curr and set_volt methods.

**Comment by dansteingart** [comment]
Thanks.  I might try to build into the teensy firmware.

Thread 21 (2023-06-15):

### ISSUE TITLE
Compilation Error for Firmware

### ISSUE THREAD

**Issue by calfredoPF** [iorodeo/potentiostat#21]
Cannot compile the firmware with Arduino version 2.10 Windows 11, it throws the following error : 
c:\Users\xxx\Documents\Arduino\potentiostat\firmware\libraries\potentiostat/ps_analog_subsystem.h:29:26:
error: 'eAnalogReference' does not name a type
29 |             static const eAnalogReference DefaultAnalogReference = AR_DEFAULT;

Please advise, thank you.

**Comment by iorodeo** [comment]
Are you building the firmware for the teensy 3.2 or the ItsyBitsy M4 Express?  

The error you are getting can occur is there is a mismatch between the dev board you have selected in  Arduino IDE and the #define option you have uncommented in the ps_hardware_defs.h file  in the firmware/libraries/potentiostat sub-directory.   In particular you will get this error if you have the Teensy 3.2 selected in the Arduino IDE while having one of the ItsyBitsy option uncommented in the ps_hardware_defs.h file.  Make sure the dev board you are building for matches the option you have commented in the ps_hardware_defs.h file.

**Comment by calfredoPF** [comment]
Thanks for your reply. I am indeed using Teensy3.2, could you advise how to
choose which teensy board to uncomment after commenting the ItsyBitsy
definition ?
    // #define HW0P2_TEENSY_10V_MICRO
    // #define HW0P1_TEENSY_10V_MICRO
    // #define HW0P1_TEENSY_10V_MILL24
    // #define HW0P1_TEENSY_10V_NANO
    // #define HW0P1_TEENSY_8V_MICRO
---
[image: photo]
*Christopher Alfredo*
Product Manager, PointFit Technology Limited

96351522 | ***@***.*** ***@***.***> |
Linkedin <https://www.linkedin.com/in/christopher-alfredo-895899265/>
*IMPORTANT: The contents of this email and any attachments are
confidential. They are intended for the named recipient(s) only. If you
have received this email by mistake, please notify the sender immediately
and do not disclose the contents to anyone or make copies thereof. *

**Comment by iorodeo** [comment]
You will want to choose this based on your hardware variant.  For example, if you you are using hardware variant V0.2 for teensy 3.2 you would select HW0P2_TEENSY_10V_MICRO.   

The  HW0P1 options  are for the older V0.1 hardware.   The most common would be HW0P1_TEENSY_10V_MICRO which is for the standard V0.1 version with the ± 1, 2, 5, 10V output ranges.  The HW0P1_TEENSY_8V_MICRO is for a V0.1 variant which has a different programmable gain amplifier for the output voltages with ± 1, 2, 4, 8V output ranges.  The remaining two options HW0P1_TEENSY_10V_NANO and HW0P1_TEENSY_10V_MILL24 are for  custom V0.1  hardware variants with nanoamp and milliamp current ranges.

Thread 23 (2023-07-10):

### ISSUE TITLE
The chart is flipped when using rodeostat teensy_shield_v0p1

### ISSUE THREAD

**Issue by chris369852147** [iorodeo/potentiostat#23]
Hello, we have encounter a problem while using rodeostat teensy_shield_v0p1.

We plot the Current-Voltage chart. Amplitude of Current in palmsens and rodeostat is different but there peak voltage location is more or less same, but the curve is flipped. 
<img width="960" alt="Screenshot 2023-07-04 12 44 01" src="https://github.com/iorodeo/potentiostat/assets/17724926/0732ea02-9f5b-4deb-afa7-7e0b591bca86">
In each case , you see current -x axis current is negative, but it should be positive.
![WhatsApp Image 2023-07-04 at 15 01 36](https://github.com/iorodeo/potentiostat/assets/17724926/0fabf207-c87e-4ece-bf39-16e24379f978) like this. 

we've check the connection of the electrodes are correct. May I ask what cause this problem and how to solve it?

**Comment by iorodeo** [comment]
What firmware version are you using?

**Comment by chris369852147** [comment]
![image](https://github.com/iorodeo/potentiostat/assets/17724926/a691fa7c-fd4b-4e77-8730-330ca36eec42)
We directly flesh the code inside TEENSY provided at your github location

**Comment by iorodeo** [comment]
OK.  The reason I ask is that between hardware versions 0.1 and 0.2 there was a polarity change on output of the transimpedance amplifier.  This is difference in sign between the two hardware versions is handled in firmware. However, in order for this to work properly the firmware needs to be built for the correct hardware version.  The first thing to do is make sure you are building the firmware for the correct hardware version.  This is set using a #define in the [ps_hardware_def.h](https://github.com/iorodeo/potentiostat/tree/master/firmware/libraries/potentiostat) file found in /firmware/libraries/potentiostat sub-directory.  There is a section at the top of this file where is says "Select your hardware version" followed by a number of #defines for selecting the specific hardware version you build for.   If you are using hardware v0.1 with the teensy 3.2 you will probably want to select the HW0P1_TEENSY_10V_MICRO option.  So that this section would look as follows

```C++
    // Select your hardware version
    // ---------------------------------------------------------------
    //#define HW0P2_ITSY_BITSY_10V_MICR0
    //#define HW0P2_ITSY_BITSY_10V_MILL10
    // #define HW0P2_TEENSY_10V_MICRO
    #define HW0P1_TEENSY_10V_MICRO
    // #define HW0P1_TEENSY_10V_MILL24
    // #define HW0P1_TEENSY_10V_NANO 
    // #define HW0P1_TEENSY_8V_MICRO
    // ---------------------------------------------------------------
```

After building and uploading the firmware the device can be queried for the hardware variant selected.  When using the web app, after connecting to the device, a section appears on the "Device Connection" page with title "Device Information" and below that is a section displaying the hardware variant string returned by the device upon connection as shown below. 

![hardware_variant_info](https://github.com/iorodeo/potentiostat/assets/56408848/60784ee5-2bd7-4b92-9f91-61a654030600)

With the Python API you can get this same information using the [get_hardware_variant](https://iorodeo.github.io/iorodeo-potentiostat-docs-build/api_reference.html#potentiostat.potentiostat.Potentiostat.get_hardware_variant)  method. 

In the example above the hardware variant string is "10V_microAmpV0.2". The V0.2 at the end indicates that the firmware I was using was built for hardware version V0.2.   If you have built firmware for the V0.1 hardware this string will be something like "10V_microAmpV0.1".

**Comment by sayansarkarnitdgp** [comment]
![Untitled](https://github.com/iorodeo/potentiostat/assets/12898769/e46cd790-2e52-4c9f-9006-63c18ee75c04)
Now we got a proper response. Thanks for your help.

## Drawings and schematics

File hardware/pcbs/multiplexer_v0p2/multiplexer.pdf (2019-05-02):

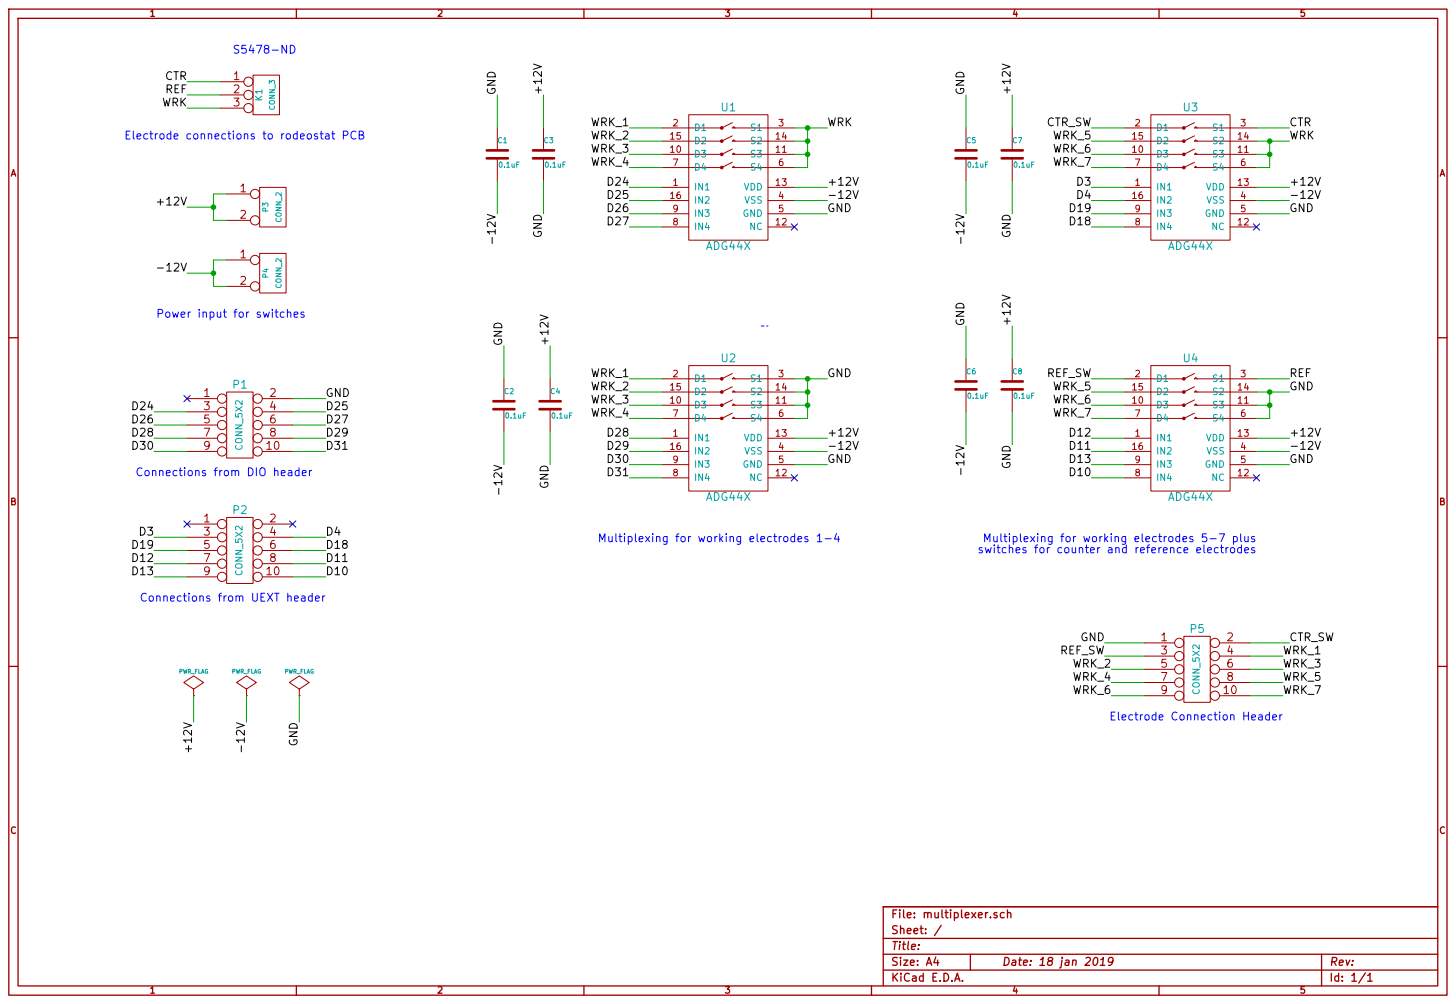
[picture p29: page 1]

Electrode connections to rodeostat PCB

Power input for switches

Connections from DIO header

switches for counter and reference electrodes

Connections from UEXT header

Id: 1/1 Title: File: multiplexer.sch
Sheet: /

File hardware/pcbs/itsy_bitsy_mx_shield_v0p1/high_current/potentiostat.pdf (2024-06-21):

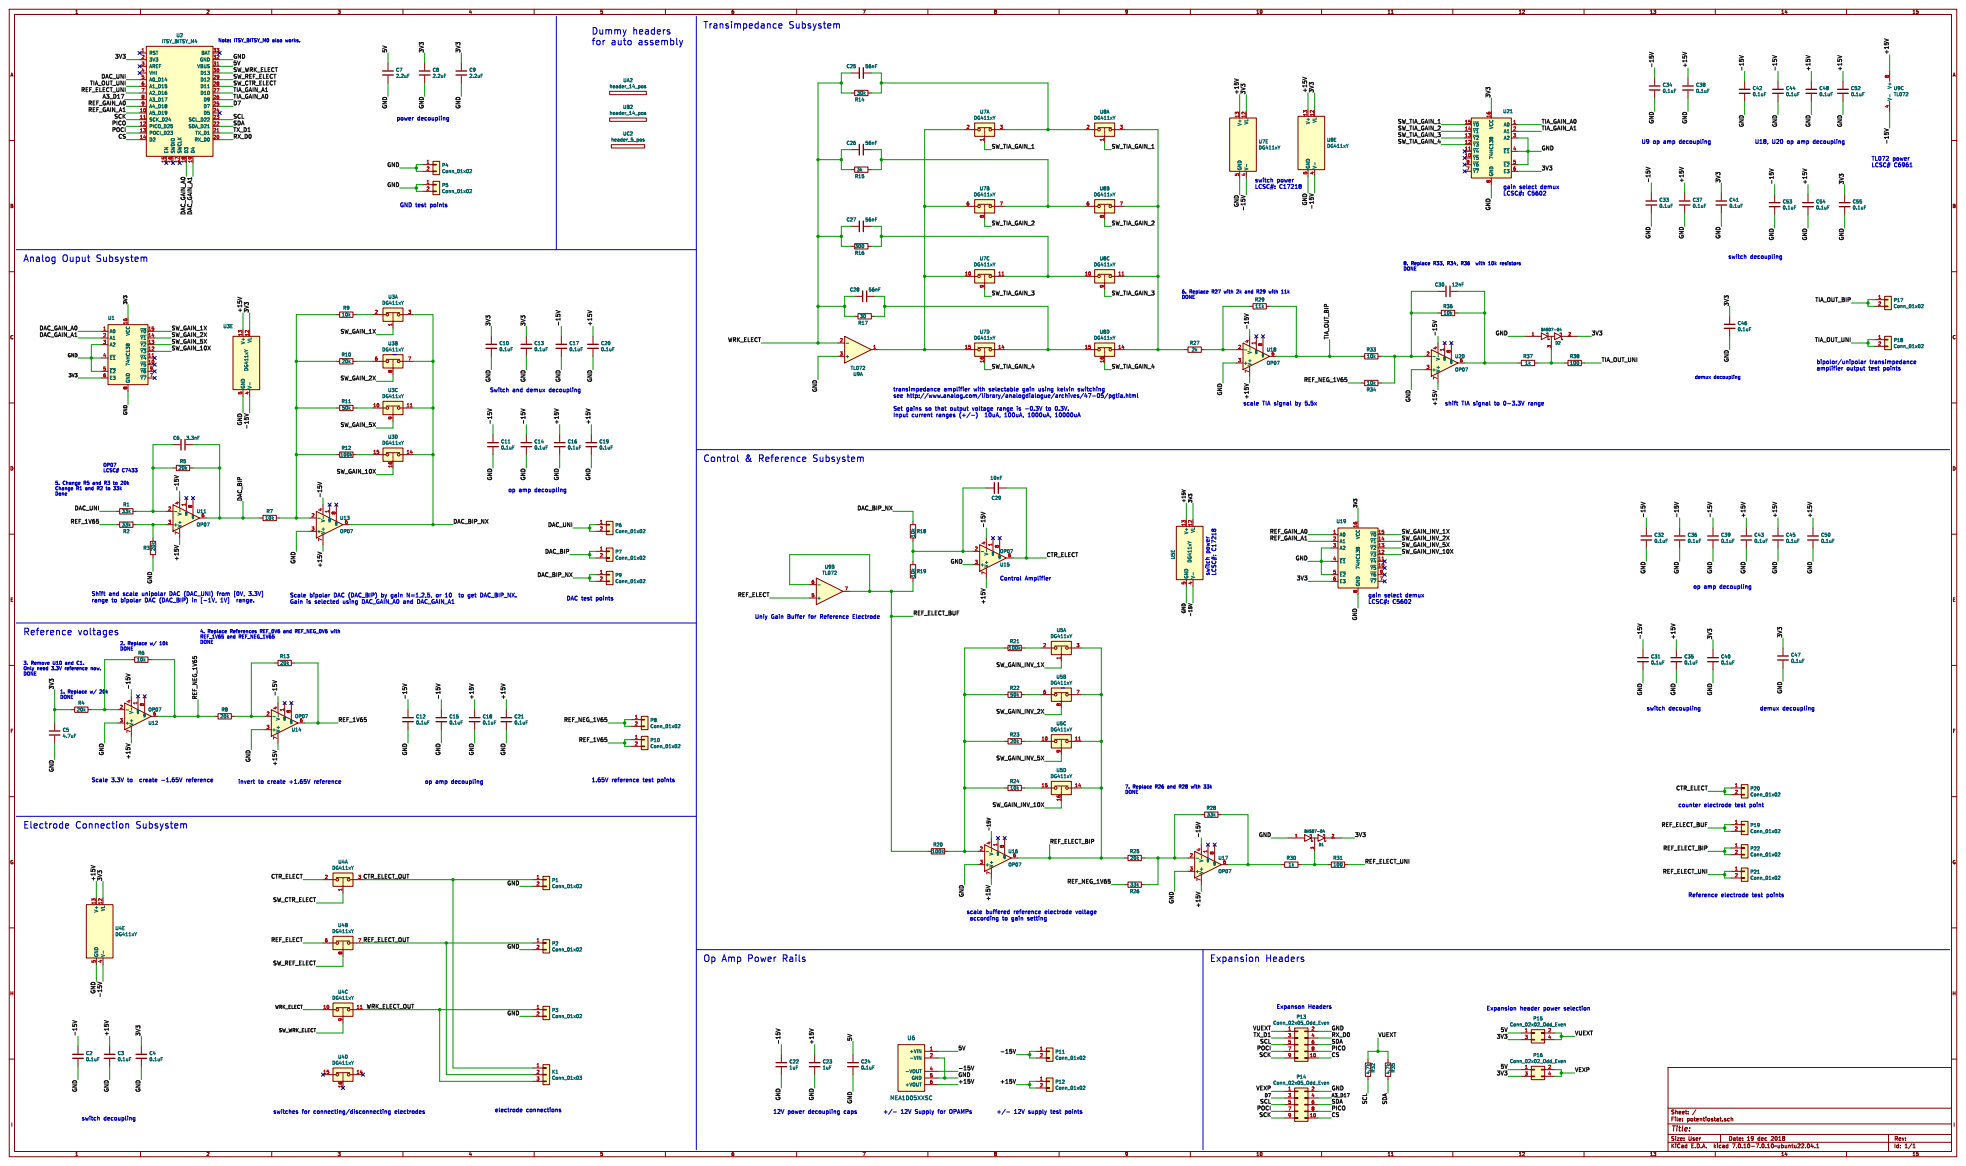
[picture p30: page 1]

gain select demux LCSC#: C5602

6. Replace R27 with 2k and R29 with 11k DONE Control & Reference Subsystem

see http://www.analog.com/library/analogdialogue/archives/47-05/pgtia.html

Switch and demux decoupling

scale TIA signal by 5.5x

5. Change R5 and R3 to 20k Change R1 and R2 to 33k Done

Gain is selected using DAC_GAIN_A0 and DAC_GAIN_A1

Uniy Gain Buffer for Reference Electrode

invert to create +1.65V reference

7. Replace R26 and R28 with 33k DONE

Id: 1/1 Title: File: potentiostat.sch Sheet: /

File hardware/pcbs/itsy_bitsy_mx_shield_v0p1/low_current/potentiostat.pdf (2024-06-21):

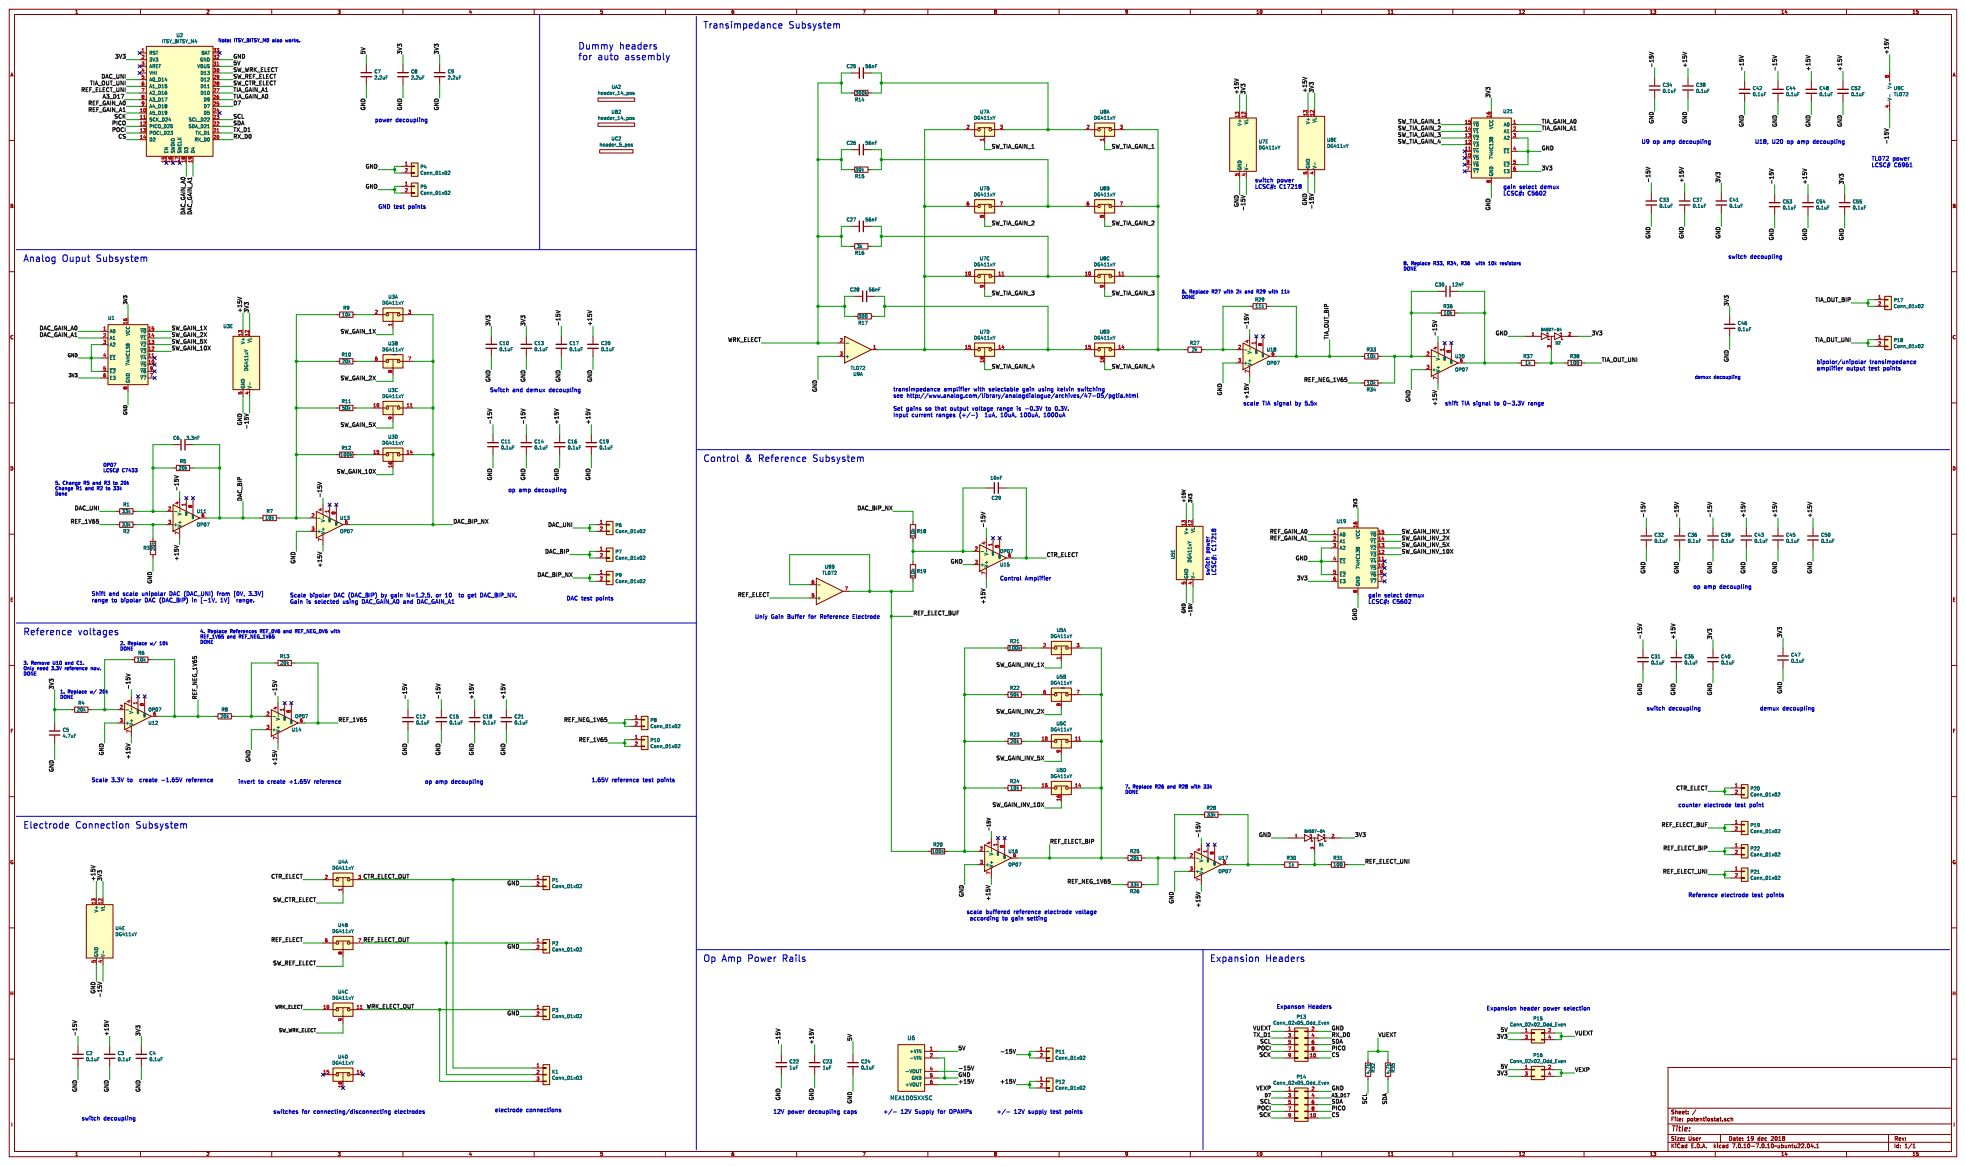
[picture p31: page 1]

gain select demux LCSC#: C5602

see http://www.analog.com/library/analogdialogue/archives/47-05/pgtia.html

Switch and demux decoupling

Gain is selected using DAC_GAIN_A0 and DAC_GAIN_A1

Uniy Gain Buffer for Reference Electrode

4. Replace References REF_0V6 and REF_NEG_0V6 with REF_1V65 and REF_NEG_1V65 DONE

invert to create +1.65V reference

Op Amp Power Rails

Expansion header power selection

Id: 1/1 Title: File: potentiostat.sch Sheet: /

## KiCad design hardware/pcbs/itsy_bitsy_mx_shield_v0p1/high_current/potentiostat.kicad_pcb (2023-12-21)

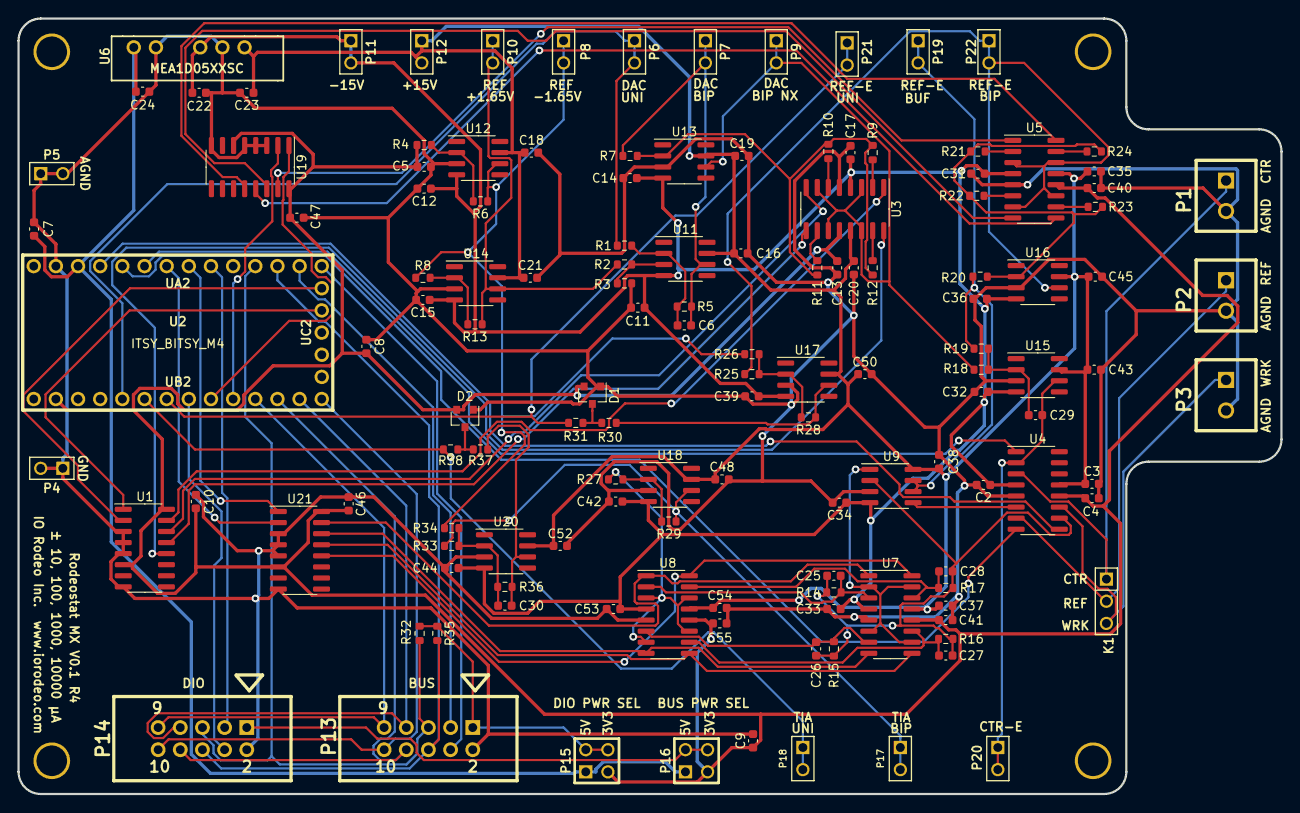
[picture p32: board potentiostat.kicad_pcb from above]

Board: 2 copper layers, 144.8 x 88.9 mm, 142 parts (0 on the bottom side), 82 nets.

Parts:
C2, C3, C4, C10, C11, C12, C13, C14, C15, C16, C17, C18, C19, C20, C21, C24, C31, C32, C33, C34, C35, C36, C37, C38, C39, C40, C41, C42, C43, C44, C45, C46, C47, C48, C50, C52, C53, C54, C55: 0.1uF; C_0603_1608Metric
C5: 4.7uF; C_0603_1608Metric
C6: 3.3nF; C_0603_1608Metric
C7, C8, C9: 2.2uF; C_0603_1608Metric
C22, C23: 1uF; C_0603_1608Metric
C25, C26, C27, C28: 56nF; C_0603_1608Metric
C29: 10nF; C_0603_1608Metric
C30: 12nF; C_0603_1608Metric
D1, D2: BAS07-04; SOT-23
H1, H2, H3, H4: VAL**; 4-40
K1: Conn_01x03; PIN_ARRAY_3X1
P1, P2, P3: Conn_01x02; CONNBLOCK2
P4, P5, P6, P7, P8, P9, P10, P11, P12, P17, P18, P19, P20, P21, P22: Conn_01x02; PIN_ARRAY_2X1
P13, P14: Conn_02x05_Odd_Even; 5X2_SHRD_HEADER
P15, P16: Conn_02x02_Odd_Even; PIN_ARRAY_2X2
R1, R2, R26, R28: 33k; R_0603_1608Metric
R3, R4, R5, R8, R10, R13, R23, R25: 20k; R_0603_1608Metric
R6, R7, R9, R18, R19, R24, R33, R34, R36: 10k; R_0603_1608Metric
R11, R22: 50k; R_0603_1608Metric
R12, R20, R21: 100k; R_0603_1608Metric
R14: 30k; R_0603_1608Metric
R15: 3k; R_0603_1608Metric
R16: 300; R_0603_1608Metric
R17: 30; R_0603_1608Metric
R27: 2k; R_0603_1608Metric
R29: 11k; R_0603_1608Metric
R30, R37: 1k; R_0603_1608Metric
R31, R38: 100; R_0603_1608Metric
R32, R35: 4.7k; R_0603_1608Metric
U1, U19, U21: 74HC138; SOIC-16_3.9x9.9mm_P1.27mm
U2: ITSY_BITSY_M4
U3, U4, U5, U7, U8: DG411xY; SOIC-16_3.9x9.9mm_P1.27mm
U6: MEA1D05XXSC; MEA1
U9: TL072; SOIC-8_3.9x4.9mm_P1.27mm
U11, U12, U13, U14, U15, U16, U17, U18, U20: OP07; SOIC-8_3.9x4.9mm_P1.27mm
UA2: header_14_pos
UB2: header_14_pos
UC2: header_5_pos

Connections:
/3V3: C4.1, C5.1, C8.1, C9.1, C10.1, C13.1, C40.1, C41.1, C46.1, C47.1, C55.1, D1.2, D2.2, P15.3, P16.3, R4.2, U1.6, U1.16, U2.2, U3.12, U4.12, U5.12, U7.12, U8.12, U19.6, U19.16, U21.6, U21.16
/5V: C7.1, C24.1, P15.1, P16.1, U2.31, U6.1
/+15V: C3.1, C16.1, C18.1, C19.1, C20.1, C21.1, C23.1, C35.1, C37.1, C38.1, C43.1, C45.1, C48.1, C50.1, C52.1, C54.1, P12.1, P12.2, U3.13, U4.13, U5.13, U6.6, U7.13, U8.13, U9.8, U11.7, U12.7, U13.7, U14.7, U15.7, U16.7, U17.7, U18.7, U20.7
/-15V: C2.1, C11.1, C12.1, C14.1, C15.1, C17.1, C22.1, C31.1, C32.1, C33.1, C34.1, C36.1, C39.1, C42.1, C44.1, C53.1, P11.1, P11.2, U3.4, U4.4, U5.4, U6.4, U7.4, U8.4, U9.4, U11.4, U12.4, U13.4, U14.4, U15.4, U16.4, U17.4, U18.4, U20.4
/A3_D17: P14.4, U2.8
/CS: P13.10, P14.10, U2.14
/CTR_ELECT: C29.1, P20.1, P20.2, U4.2, U15.6
/CTR_ELECT_OUT: K1.1, P1.1, U4.3
/D7: P14.3, U2.25
/DAC_BIP: C6.1, P7.1, P7.2, R5.1, R7.2, U11.6
/DAC_BIP_NX: P9.1, P9.2, R18.2, U3.3, U3.7, U3.11, U3.14, U13.6
/DAC_GAIN_A0: U1.1, U2.18
/DAC_GAIN_A1: U1.2, U2.19
/DAC_UNI: P6.1, P6.2, R1.2, U2.5
/GND: C2.2, C3.2, C4.2, C5.2, C7.2, C8.2, C9.2, C10.2, C11.2, C12.2, C13.2, C14.2, C15.2, C16.2, C17.2, C18.2, C19.2, C20.2, C21.2, C22.2, C23.2, C24.2, C31.2, C32.2, C33.2, C34.2, C35.2, C36.2, C37.2, C38.2, C39.2, C40.2, C41.2, C42.2, C43.2, C44.2, C45.2, C46.2, C47.2, C48.2, C50.2, C52.2, C53.2, C54.2, C55.2, D1.1, D2.1, P1.2, P2.2, P3.2, P4.1, P4.2, P5.1, P5.2, P13.2, P14.2, R3.2, U1.3, U1.4, U1.5, U1.8, U2.32, U3.5, U4.5, U5.5, U6.2, U6.5, U7.5, U8.5, U9.3, U12.3, U13.3, U14.3, U15.3, U16.3, U17.3, U18.3, U19.3, U19.4, U19.5, U19.8, U20.3, U21.3, U21.4, U21.5, U21.8
/PICO: P13.8, P14.8, U2.12
/POCI: P13.7, P14.7, U2.13
/REF_1V65: P10.1, P10.2, R2.2, R13.1, U14.6
/REF_ELECT: U4.6, U9.5
/REF_ELECT_BIP: P22.1, P22.2, R25.2, U5.3, U5.7, U5.11, U5.14, U16.6
/REF_ELECT_BUF: P19.1, P19.2, R19.1, R20.2, U9.6, U9.7
/REF_ELECT_OUT: K1.2, P2.1, U4.7
/REF_ELECT_UNI: P21.1, P21.2, R31.1, U2.7
/REF_GAIN_A0: U2.9, U19.1
/REF_GAIN_A1: U2.10, U19.2
/REF_NEG_1V65: P8.1, P8.2, R6.1, R8.2, R26.2, R34.2, U12.6
/RX_D0: P13.4, U2.20
/SCK: P13.9, P14.9, U2.11
/SCL: P13.5, P14.5, R32.2, U2.23
/SDA: P13.6, P14.6, R35.2, U2.22
/SW_CTR_ELECT: U2.28, U4.1
/SW_GAIN_1X: U1.15, U3.1
/SW_GAIN_2X: U1.14, U3.8
/SW_GAIN_5X: U1.13, U3.9
/SW_GAIN_10X: U1.12, U3.16
/SW_GAIN_INV_1X: U5.1, U19.15
/SW_GAIN_INV_2X: U5.8, U19.14
/SW_GAIN_INV_5X: U5.9, U19.13
/SW_GAIN_INV_10X: U5.16, U19.12
/SW_REF_ELECT: U2.29, U4.8
/SW_TIA_GAIN_1: U7.1, U8.1, U21.15
/SW_TIA_GAIN_2: U7.8, U8.8, U21.14
/SW_TIA_GAIN_3: U7.9, U8.9, U21.13
/SW_TIA_GAIN_4: U7.16, U8.16, U21.12
/SW_WRK_ELECT: U2.30, U4.9
/TIA_GAIN_A0: U2.26, U21.1
/TIA_GAIN_A1: U2.27, U21.2
/TIA_OUT_BIP: P17.1, P17.2, R29.1, R33.2, U18.6
/TIA_OUT_UNI: P18.1, P18.2, R38.1, U2.6
/TX_D1: P13.3, U2.21
/VEXP: P14.1, P16.2, P16.4
/VUEXT: P13.1, P15.2, P15.4, R32.1, R35.1
/WRK_ELECT: C25.2, C26.2, C27.2, C28.2, R14.2, R15.2, R16.2, R17.2, U4.10, U9.2
/WRK_ELECT_OUT: K1.3, P3.1, U4.11
unnamed: C6.2, R1.1, R5.2, U11.2
unnamed: C25.1, R14.1, U7.3, U8.2
unnamed: C26.1, R15.1, U7.7, U8.6
unnamed: C27.1, R16.1, U7.11, U8.10
unnamed: C28.1, R17.1, U7.14, U8.15
unnamed: C29.2, R18.1, R19.2, U15.2
unnamed: C30.1, R36.1, R37.2, U20.6
unnamed: C30.2, R33.1, R34.1, R36.2, U20.2
unnamed: D1.3, R30.1, R31.2
unnamed: D2.3, R37.1, R38.2
unnamed: R2.1, R3.1, U11.3
unnamed: R4.1, R6.2, U12.2
unnamed: R9.1, U3.2
unnamed: R10.1, U3.6
unnamed: R7.1, R9.2, R10.2, R11.2, R12.2, U13.2
unnamed: R11.1, U3.10
unnamed: R12.1, U3.15
unnamed: R8.1, R13.2, U14.2
unnamed: R20.1, R21.2, R22.2, R23.2, R24.2, U16.2
unnamed: R21.1, U5.2
unnamed: R22.1, U5.6
unnamed: R23.1, U5.10
unnamed: R24.1, U5.15
unnamed: R25.1, R26.1, R28.2, U17.2
unnamed: R27.1, R29.2, U18.2
unnamed: R27.2, U8.3, U8.7, U8.11, U8.14
unnamed: R28.1, R30.2, U17.6
unnamed: U7.2, U7.6, U7.10, U7.15, U9.1

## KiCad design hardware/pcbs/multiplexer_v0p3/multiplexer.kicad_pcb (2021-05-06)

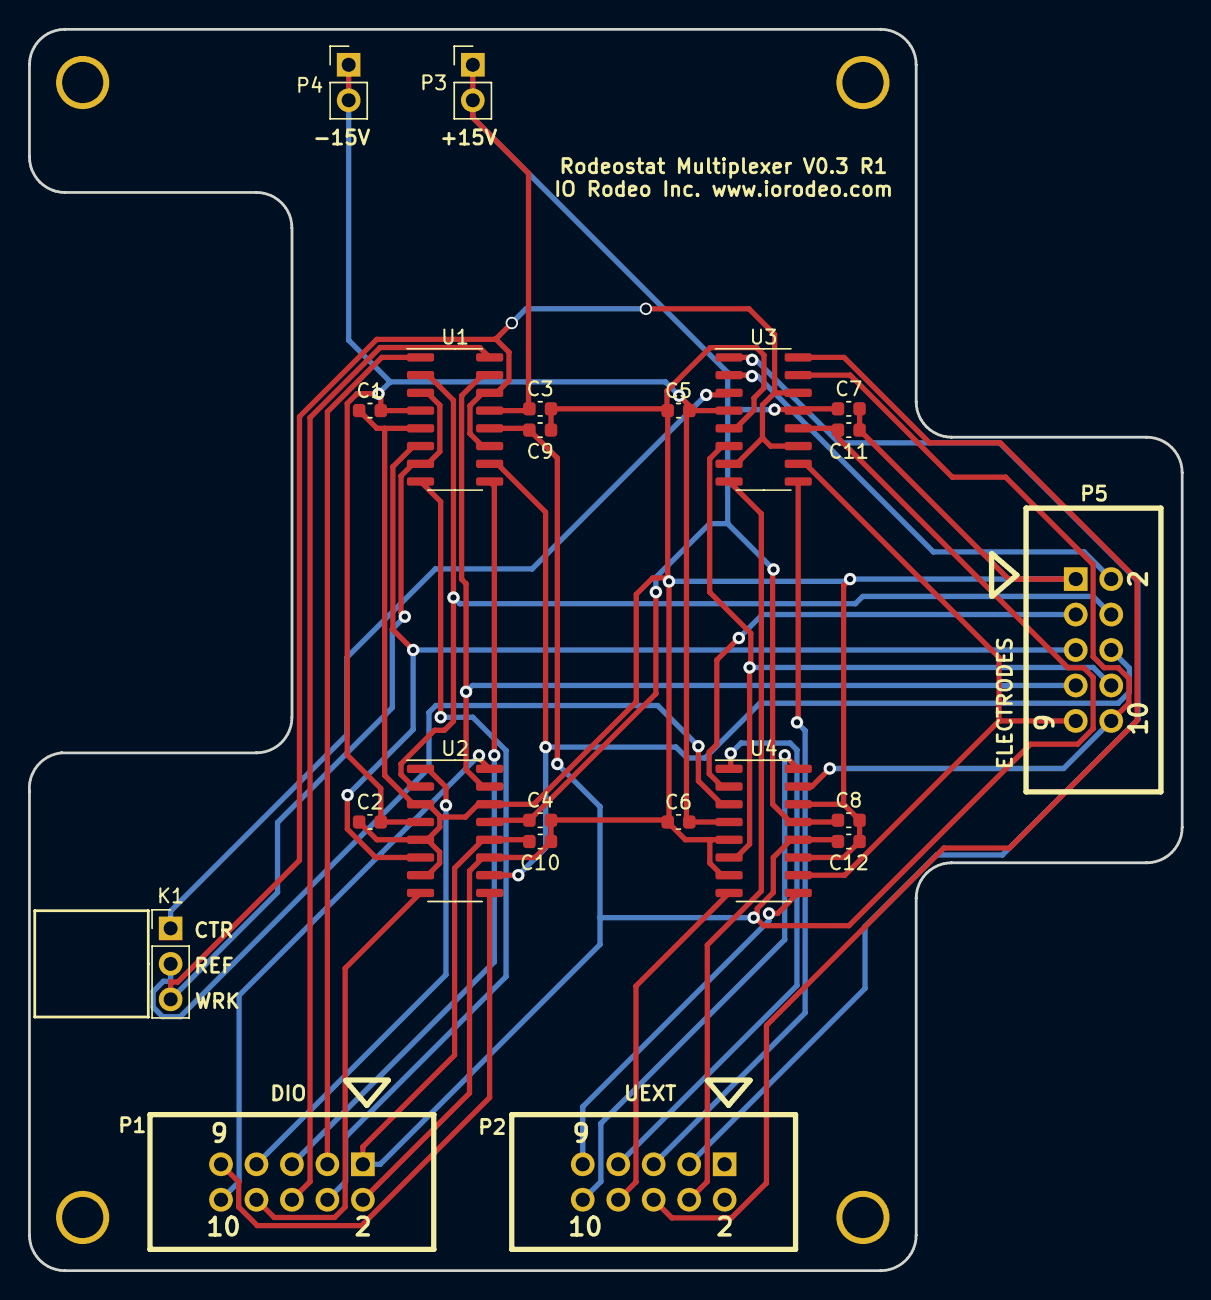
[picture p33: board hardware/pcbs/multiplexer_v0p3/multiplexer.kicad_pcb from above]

Board: 2 copper layers, 82.6 x 88.9 mm, 26 parts (0 on the bottom side), 32 nets.

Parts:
4-40: VAL**; 4-40
C1, C2, C3, C4, C5, C6, C7, C8, C9, C10, C11, C12: 0.1uF; C_0603_1608Metric
K1: CONN_3; PinHeader_1x03_P2.54mm_Vertical
M1, M2, M3: VAL**; 4-40
P1, P2, P5: CONN_5X2; 5X2_SHRD_HEADER
P3, P4: CONN_2; PinHeader_1x02_P2.54mm_Vertical
U1, U2, U3, U4: DG411xY; SOIC-16_3.9x9.9mm_P1.27mm

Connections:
/3V3: C9.1, C10.1, C11.1, C12.1, P1.1, U1.12, U2.12, U3.12, U4.12
/+15V: C3.1, C4.1, C7.1, C8.1, P3.1, P3.2, U1.13, U2.13, U3.13, U4.13
/-15V: C1.2, C2.2, C5.2, C6.2, P4.1, P4.2, U1.4, U2.4, U3.4, U4.4
/CTR: K1.1, U3.3
/CTR_SW: P5.2, U3.2
/D3: P2.3, U3.1
/D4: P2.4, U3.8
/D10: P2.10, U4.16
/D11: P2.8, U4.8
/D12: P2.7, U4.1
/D13: P2.9, U4.9
/D18: P2.6, U3.16
/D19: P2.5, U3.9
/D24: P1.3, U1.1
/D25: P1.4, U1.8
/D26: P1.5, U1.9
/D27: P1.6, U1.16
/D28: P1.7, U2.1
/D29: P1.8, U2.8
/D30: P1.9, U2.9
/D31: P1.10, U2.16
/GND: C1.1, C2.1, C3.2, C4.2, C5.1, C6.1, C7.2, C8.2, C9.2, C10.2, C11.2, C12.2, P1.2, P5.1, U1.5, U2.3, U2.5, U2.7, U2.11, U2.14, U3.5, U4.5, U4.7, U4.11, U4.14
/REF: K1.2, U4.3
/REF_SW: P5.3, U4.2
/WRK: K1.3, U1.3, U1.7, U1.11, U1.14, U3.7, U3.11, U3.14
/WRK_1: P5.4, U1.2, U2.2
/WRK_2: P5.5, U1.6, U2.6
/WRK_3: P5.6, U1.10, U2.10
/WRK_4: P5.7, U1.15, U2.15
/WRK_5: P5.8, U3.6, U4.6
/WRK_6: P5.9, U3.10, U4.10
/WRK_7: P5.10, U3.15, U4.15

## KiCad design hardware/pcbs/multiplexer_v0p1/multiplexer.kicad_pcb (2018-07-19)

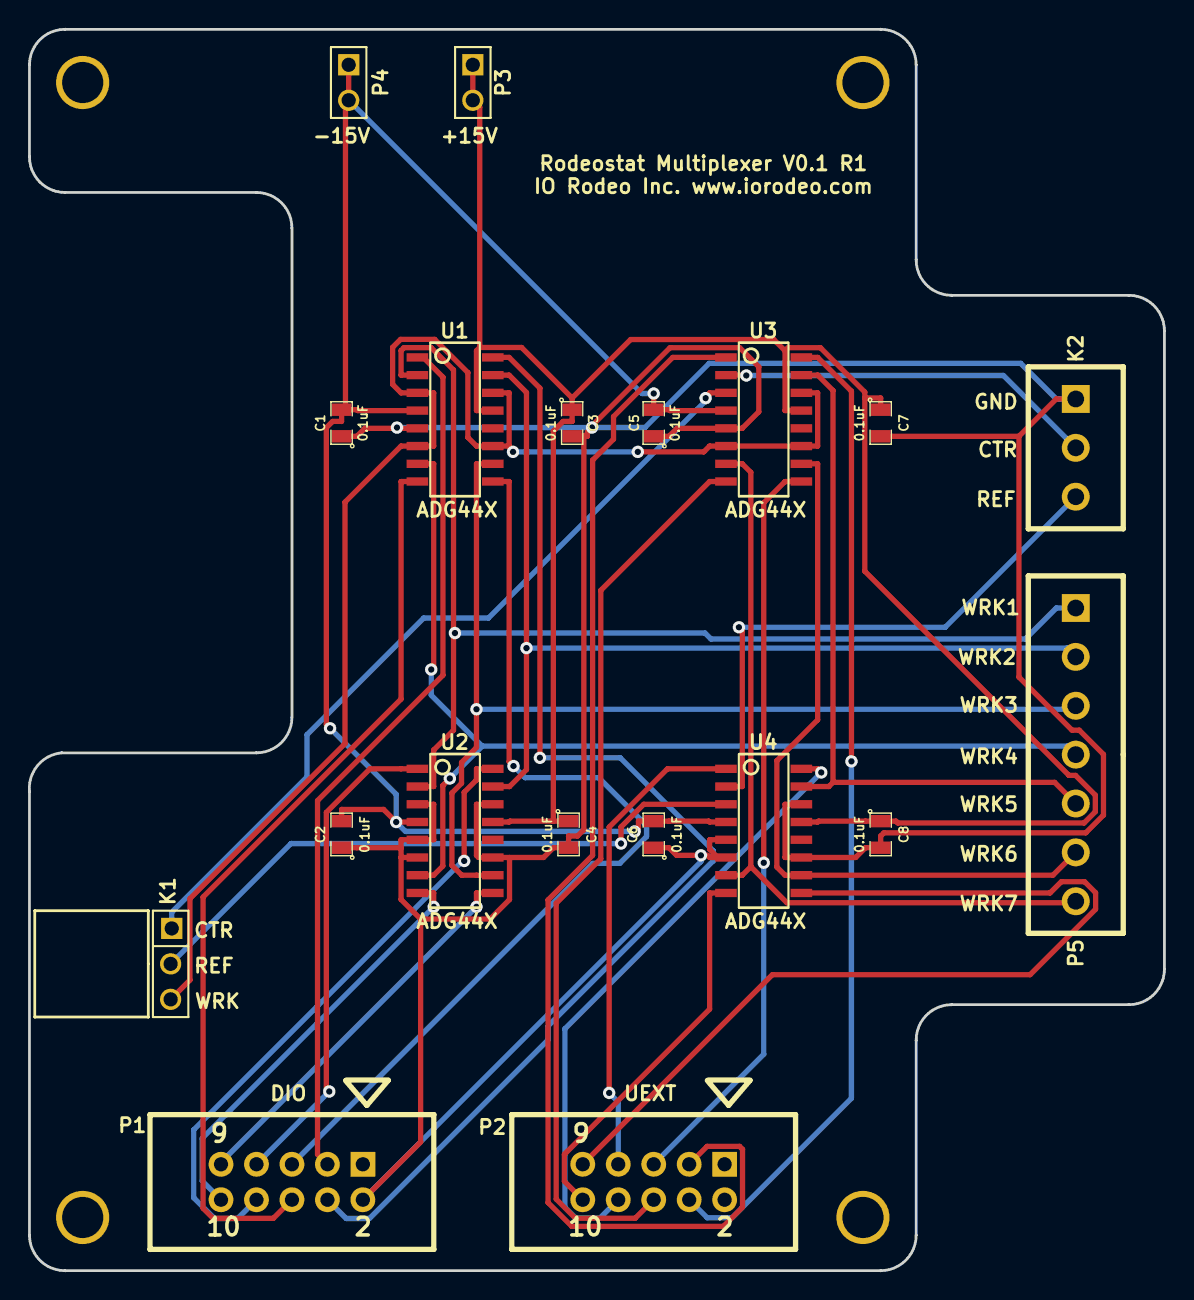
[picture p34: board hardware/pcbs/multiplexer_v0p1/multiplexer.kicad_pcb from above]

Board: 2 copper layers, 81.3 x 88.9 mm, 23 parts (0 on the bottom side), 31 nets.

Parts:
4-40: VAL**; 4-40
C1, C2, C3, C4, C5, C6, C7, C8: 0.1uF; SM0805
K1: CONN_3; PIN_ARRAY_3X1
K2: CONN_3; CONNBLOCK3
M1, M2, M3: VAL**; 4-40
P1, P2: CONN_5X2; 5X2_SHRD_HEADER
P3, P4: CONN_2; PIN_ARRAY_2X1
P5: CONN_7; CONNBLOCK7
U1, U2, U3, U4: ADG44X; 16-SOIC-0154

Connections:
/+15V: C3.1, C4.1, C7.1, C8.1, P3.1, P3.2, U1.13, U2.13, U3.13, U4.13
/-15V: C1.2, C2.2, C5.2, C6.2, P4.1, P4.2, U1.4, U2.4, U3.4, U4.4
/CTR: K1.1, U3.3
/CTR_SW: K2.2, U3.2
/D3: P2.3, U3.1
/D4: P2.4, U3.16
/D10: P2.10, U4.8
/D11: P2.8, U4.16
/D12: P2.7, U4.1
/D13: P2.9, U4.9
/D18: P2.6, U3.8
/D19: P2.5, U3.9
/D24: P1.3, U1.1
/D25: P1.4, U1.16
/D26: P1.5, U1.9
/D27: P1.6, U1.8
/D28: P1.7, U2.1
/D29: P1.8, U2.16
/D30: P1.9, U2.9
/D31: P1.10, U2.8
/GND: C1.1, C2.1, C3.2, C4.2, C5.1, C6.1, C7.2, C8.2, K2.1, P1.2, U1.5, U2.3, U2.5, U2.6, U2.11, U2.14, U3.5, U4.5, U4.6, U4.11, U4.14
/REF: K1.2, U4.3
/REF_SW: K2.3, U4.2
/WRK: K1.3, U1.3, U1.6, U1.11, U1.14, U3.6, U3.11, U3.14
/WRK_1: P5.1, U1.2, U2.2
/WRK_2: P5.2, U1.15, U2.15
/WRK_3: P5.3, U1.10, U2.10
/WRK_4: P5.4, U1.7, U2.7
/WRK_5: P5.5, U3.15, U4.15
/WRK_6: P5.6, U3.10, U4.10
/WRK_7: P5.7, U3.7, U4.7

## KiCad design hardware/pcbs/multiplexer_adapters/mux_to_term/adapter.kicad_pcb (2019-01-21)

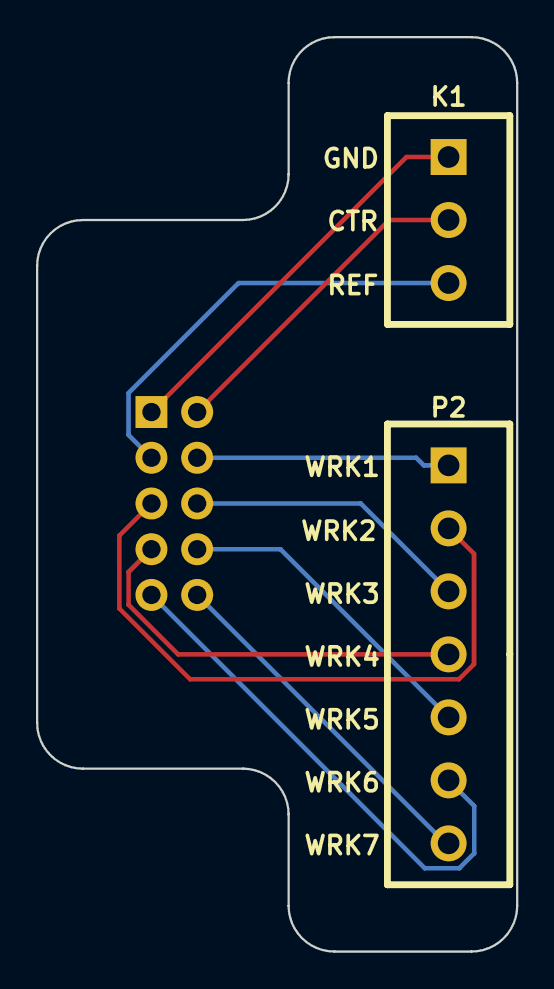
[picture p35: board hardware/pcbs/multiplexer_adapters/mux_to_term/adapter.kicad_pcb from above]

Board: 2 copper layers, 26.7 x 50.8 mm, 3 parts (1 on the bottom side), 10 nets.

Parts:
K1: CONN_3; CONNBLOCK3
P1: CONN_5X2; 5X2_SHRD_HEADER_FEMALE
P2: CONN_7; CONNBLOCK7

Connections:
/CTR_SW: K1.2, P1.2
/GND: K1.1, P1.1
/REF_SW: K1.3, P1.3
/WRK_1: P1.4, P2.1
/WRK_2: P1.5, P2.2
/WRK_3: P1.6, P2.3
/WRK_4: P1.7, P2.4
/WRK_5: P1.8, P2.5
/WRK_6: P1.9, P2.6
/WRK_7: P1.10, P2.7

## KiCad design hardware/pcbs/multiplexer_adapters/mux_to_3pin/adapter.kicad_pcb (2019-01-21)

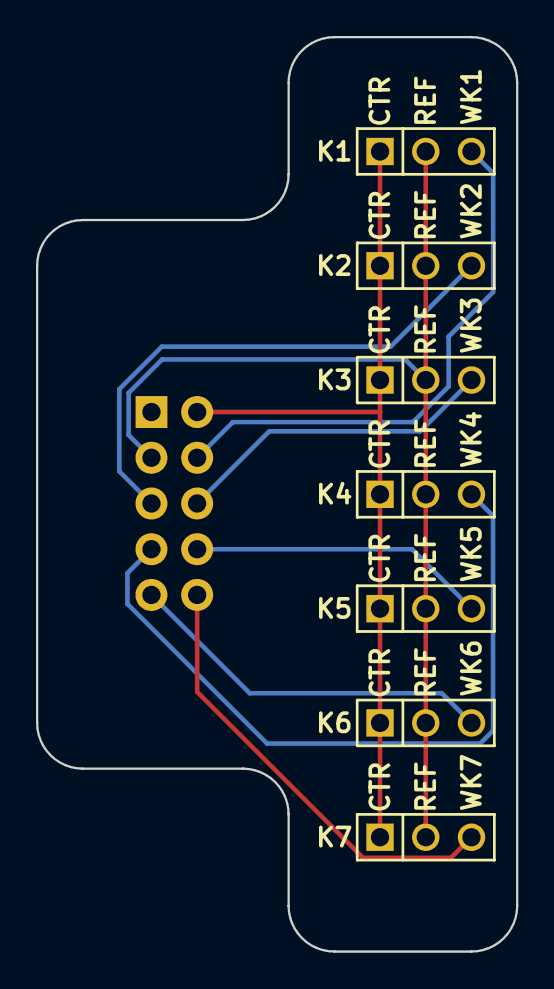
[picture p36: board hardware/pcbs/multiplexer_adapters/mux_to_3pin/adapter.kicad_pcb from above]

Board: 2 copper layers, 26.7 x 50.8 mm, 8 parts (1 on the bottom side), 9 nets.

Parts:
K1, K2, K3, K4, K5, K6, K7: CONN_3; PIN_ARRAY_3X1
P1: CONN_5X2; 5X2_SHRD_HEADER_FEMALE

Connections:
/CTR_SW: K1.1, K2.1, K3.1, K4.1, K5.1, K6.1, K7.1, P1.2
/REF_SW: K1.2, K2.2, K3.2, K4.2, K5.2, K6.2, K7.2, P1.3
/WRK_1: K1.3, P1.4
/WRK_2: K2.3, P1.5
/WRK_3: K3.3, P1.6
/WRK_4: K4.3, P1.7
/WRK_5: K5.3, P1.8
/WRK_6: K6.3, P1.9
/WRK_7: K7.3, P1.10

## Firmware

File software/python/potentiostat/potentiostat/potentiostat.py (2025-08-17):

"""
============
potentiostat
============

    This module implements the serial interface to the Rodeostat open source
    Potentiostat.

    :copyright: (c) 2017 by IO Rodeo 
    :license: MIT, see LICENSE.txt for more details.
"""
from __future__ import print_function
import serial
import time
import json
import atexit
import contextlib
import progressbar
import os
try:
    import cPickle as pickle
except ImportError:
    import pickle

# Json message keys
CommandKey = 'command'
ResponseKey = 'response'
MessageKey = 'message'
SuccessKey = 'success'
TestKey = 'test'
ParamKey = 'param'
TimeKey = 't'
VoltKey = 'v'
CurrKey = 'i'
ChanKey = 'n'
LimitErrKey = 'le'
RefVoltKey = 'r'
VoltRangeKey = 'voltRange'
CurrRangeKey = 'currRange'
DeviceIdKey = 'deviceId'
SamplePeriodKey = 'samplePeriod'
TestDoneTimeKey = 'testDoneTime'
StepArrayKey = 'step'
TestNameArrayKey = 'testNames'
VersionKey = 'version'
VariantKey = 'variant'
MuxEnabledKey = 'muxEnabled'
MuxChannelKey = 'muxChannel'
ConnectedKey = 'connected'
AutoConnectKey = "autoConnect"

# Commands
RunTestCmd  = 'runTest'
StopTestCmd = 'stopTest'
GetVoltCmd = 'getVolt'
SetVoltCmd = 'setVolt'
GetCurrCmd = 'getCurr'
GetRefVoltCmd = 'getRefVolt'
GetParamCmd = 'getParam'
SetParamCmd = 'setParam'
GetVoltRangeCmd = 'getVoltRange'
SetVoltRangeCmd = 'setVoltRange'
GetCurrRangeCmd = 'getCurrRange'
SetCurrRangeCmd = 'setCurrRange'
GetDeviceIdCmd = 'getDeviceId'
SetDeviceIdCmd = 'setDeviceId'
GetSamplePeriodCmd = 'getSamplePeriod'
SetSamplePeriodCmd = 'setSamplePeriod'
GetTestDoneTimeCmd = 'getTestDoneTime'
GetTestNamesCmd = 'getTestNames'
GetVersionCmd = 'getVersion'
GetVariantCmd = 'getVariant'

SetMuxEnabledCmd = 'setMuxEnabled'
GetMuxEnabledCmd = 'getMuxEnabled'
SetEnabledMuxChanCmd = 'setEnabledMuxChannels'
GetEnabledMuxChanCmd = 'getEnabledMuxChannels'
GetMuxTestNamesCmd = 'getMuxTestNames'
SetMuxRefElectConnCmd = "setMuxRefElectConnected"
GetMuxRefElectConnCmd = "getMuxRefElectConnected"
SetMuxCtrElectConnCmd = "setMuxCtrElectConnected"
GetMuxCtrElectConnCmd = "getMuxCtrElectConnected"
SetMuxWrkElectConnCmd = "setMuxWrkElectConnected"
GetMuxWrkElectConnCmd = "getMuxWrkElectConnected"
DisconnAllMuxElectCmd = "disconnectAllMuxElect"

SetRefElectConnCmd = "setRefElectConnected"
GetRefElectConnCmd = "getRefElectConnected"
SetCtrElectConnCmd = "setCtrElectConnected"
GetCtrElectConnCmd = "getCtrElectConnected"
SetWrkElectConnCmd = "setWrkElectConnected"
GetWrkElectConnCmd = "getWrkElectConnected"
SetAllElectConnCmd = "setAllElectConnected"
GetAllElectConnCmd = "getAllElectConnected"
SetElectAutoConnCmd = "setElectAutoConnect"        
GetElectAutoConnCmd = "getElectAutoConnect"         
SetRefElectVoltRangeCmd = "setRefElectVoltRange"
GetRefElectVoltRangeCmd = "getRefElectVoltRange"
GetHardwareVersionCmd = "getHardwareVersion"        

# Hardware version strings
HardwareVersionDefault = "HW0.1 (default)"
HardwareVersion0p1 = "HW0.1"
HardwareVersion0p2 = "HW0.2"

# Voltage ranges
VoltRange1V = '1V'
VoltRange2V = '2V'
VoltRange4V = '4V'
VoltRange5V = '5V'
VoltRange8V = '8V'
VoltRange10V = '10V'
VoltRangeList_8V = [VoltRange1V, VoltRange2V, VoltRange4V, VoltRange8V]
VoltRangeList_10V = [VoltRange1V, VoltRange2V, VoltRange5V, VoltRange10V]

HwVariantToVoltRangesDict = {
        'nanoAmpV0.1'         : VoltRangeList_10V, 
        'microAmpV0.1'        : VoltRangeList_10V, 
        'milliAmpV0.1'        : VoltRangeList_10V, 
        'AD8250_nanoAmpV0.1'  : VoltRangeList_10V, 
        'AD8250_microAmpV0.1' : VoltRangeList_10V, 
        'AD8250_milliAmpV0.1' : VoltRangeList_10V, 
        'AD8251_nanoAmpV0.1'  : VoltRangeList_8V,  
        'AD8251_microAmpV0.1' : VoltRangeList_8V, 
        'AD8251_milliAmpV0.1' : VoltRangeList_8V, 
        '10V_nanoAmpV0.2'     : VoltRangeList_10V, 
        '10V_microAmpV0.2'    : VoltRangeList_10V, 
        '10V_milliAmpV0.2'    : VoltRangeList_10V, 
        '10V_10MilliAmpV0.2'  : VoltRangeList_10V,
        '10V_24MilliAmpV0.2'  : VoltRangeList_10V,
        }

# Current Ranges
CurrRange60nA = '60nA'
CurrRange100nA = '100nA'
CurrRange1uA = '1uA'
CurrRange10uA = '10uA'
CurrRange100uA = '100uA'
CurrRange1000uA = '1000uA'
CurrRange10000uA = '10000uA'
CurrRange12000uA = '12000uA'
CurrRange24000uA = '24000uA'

CurrRangeListNanoAmp = [CurrRange1uA, CurrRange10uA, CurrRange100nA, CurrRange60nA]
CurrRangeListMicroAmp = [CurrRange1uA, CurrRange10uA, CurrRange100uA, CurrRange1000uA]
CurrRangeList10MilliAmp = [CurrRange10uA, CurrRange100uA, CurrRange1000uA, CurrRange10000uA]
CurrRangeList24MilliAmp = [CurrRange100uA, CurrRange1000uA, CurrRange12000uA, CurrRange24000uA]

HwVariantToCurrRangesDict = {
        'nanoAmpV0.1'         :  CurrRangeListNanoAmp,
        'microAmpV0.1'        :  CurrRangeListMicroAmp, 
        'milliAmpV0.1'        :  CurrRangeList24MilliAmp,
        'AD8250_nanoAmpV0.1'  :  CurrRangeListNanoAmp,
        'AD8250_microAmpV0.1' :  CurrRangeListMicroAmp, 
        'AD8250_milliAmpV0.1' :  CurrRangeList24MilliAmp,
        'AD8251_nanoAmpV0.1'  :  CurrRangeListNanoAmp,
        'AD8251_microAmpV0.1' :  CurrRangeListMicroAmp, 
        'AD8251_milliAmpV0.1' :  CurrRangeList24MilliAmp,
        '10V_nanoAmpV0.2'     :  CurrRangeListNanoAmp,
        '10V_microAmpV0.2'    :  CurrRangeListMicroAmp, 
        '10V_milliAmpV0.2'    :  CurrRangeList24MilliAmp,
        '10V_10MilliAmpV0.2'  :  CurrRangeList10MilliAmp,
        '10V_24MilliAmpV0.2'  :  CurrRangeList24MilliAmp,
        }

TimeUnitToScale = {'s': 1.e-3, 'ms': 1}

MinimumFirmwareVersionForMux = '0.0.5'

TxtOutputFileType = 0
PklOutputFileType = 1

class Potentiostat(serial.Serial):

    """Provides a high level interface for serial communications with the Rodeostat. 

    Args:
        port (str): serial port associated with the Rodeostat, e.g. /dev/ttyACM0, COM1, etc.

    Keyword Args:
        timeout (float): serial port ready timeout (seconds)

    """

    
    ResetSleepDt = 0.0
    Baudrate = 115200
    DefaultTimeout = 2.0

    def __init__(self, port, timeout=DefaultTimeout):
        params = {'baudrate': self.Baudrate, 'timeout': timeout}
        super(Potentiostat,self).__init__(port,**params)
        time.sleep(self.ResetSleepDt)
        self.test_running = False
        atexit.register(self.atexit_cleanup)
        while self.inWaiting() > 0:
            val = self.read()
        self.hardware_variant = self.get_hardware_variant()
        self.firmware_version = self.get_firmware_version()
        self.hardware_version = self.get_hardware_version()


    def get_hardware_variant(self):
        """Returns a string representing the hardware variant.

        Returns:
            str: hardware variant, e.g. '10V_microAmpV0.2'

        """
        cmd_dict = {CommandKey: GetVariantCmd}
        msg_dict = self.send_cmd(cmd_dict)
        return msg_dict[ResponseKey][VariantKey]


    def stop_test(self,rsp=True):
        """Stops (any) currently running tests. """
        cmd_dict = {CommandKey: StopTestCmd}
        msg_dict = self.send_cmd(cmd_dict, rsp=rsp)


    def get_volt(self):
        """Returns the output voltage setting, i.e, the potential between the
        working and reference electrode. 

        Returns:
            float: output voltage setting, units (V)

        """
        cmd_dict = {CommandKey: GetVoltCmd}
        msg_dict = self.send_cmd(cmd_dict)
        volt = msg_dict[ResponseKey][VoltKey]
        return volt


    def set_volt(self,volt):
        """Sets the output voltage setting, i.e., the potential between the
        working and reference electrode. 

        Args:
            volt (float): output voltage setting, units (V)

        Returns:
            float: output voltage setting, units (V)

        """
        cmd_dict = {CommandKey: SetVoltCmd, VoltKey: volt}
        msg_dict = self.send_cmd(cmd_dict)
        volt = msg_dict[ResponseKey][VoltKey]
        return volt


    def get_curr(self):
        """Gets an immediate measurement of the working electrode current. 

        Returns:
            float: working electrode current, units (uA)

        """
        cmd_dict = {CommandKey: GetCurrCmd}
        msg_dict = self.send_cmd(cmd_dict)
        curr = msg_dict[ResponseKey][CurrKey]
        return curr


    def get_ref_volt(self):
        """Gets an immediate measurement of the potential between the working
        and reference electrode. 

        Returns:
            float: potential between working and reference electrode, units (V)

        """
        cmd_dict = {CommandKey: GetRefVoltCmd}
        msg_dict = self.send_cmd(cmd_dict)
        volt = msg_dict[ResponseKey][RefVoltKey]
        return volt


    def get_param(self,testname):
        """Returns the current values of the parameters for the specified
        voltammetric test. 

        Args:
            testname (str): name of voltammetric test, e.g., 'cyclic'

        Returns:
            dict: current values of test parameters 

        """
        cmd_dict = {CommandKey: GetParamCmd, TestKey: testname} 
        msg_dict = self.send_cmd(cmd_dict)
        return msg_dict[ResponseKey][ParamKey]


    def set_param(self,testname,param):
        """Sets the parameters for the specified voltammetric test.

        Args:
            testname (str): name of voltammetric test
            param   (dict): desired test parameters 

        Returns:
            dict: test parameters for testname (from device)

        """
        cmd_dict = {CommandKey: SetParamCmd, TestKey: testname, ParamKey: param}
        msg_dict = self.send_cmd(cmd_dict)
        return msg_dict[ResponseKey][ParamKey]


    def set_volt_range(self,volt_range):
        """Sets the output voltage range (V)- used when setting output voltage
        manually.

        Args:
            volt_range (str): desired output voltage range, e.g., '1V'

        Returns:
            dict: voltage range (from device)

        """
        if not volt_range in self.get_all_volt_range():
            raise ValueError('unknown voltage range')
        cmd_dict = {CommandKey: SetVoltRangeCmd, VoltRangeKey: volt_range}
        msg_dict = self.send_cmd(cmd_dict)
        return msg_dict[ResponseKey][VoltRangeKey]


    def get_volt_range(self):
        """Gets the current value for the output voltage range (V).

        Returns:
            dict: voltage range (from device)

        """
        cmd_dict = {CommandKey: GetVoltRangeCmd}
        msg_dict = self.send_cmd(cmd_dict)
        return msg_dict[ResponseKey][VoltRangeKey]


    def get_all_volt_range(self):
        """Gets a list of the voltage ranges supported by the device.

        Returns:
            list: available voltage ranges, e.g., ['1V', '2V', '5V', '10V']

        """
        return HwVariantToVoltRangesDict[self.hardware_variant]


    def set_curr_range(self,curr_range):
        """Sets the range setting for measuring working electrode (uA).

        Args:
            curr_range (str): the desired workign electrode current range setting, e.g., '10uA'

        Returns:
            str: working electrode current range setting (from device), e.g. '10uA'

        """
        if not curr_range in self.get_all_curr_range(): 
            raise ValueError('unknown current range')
        cmd_dict = {CommandKey: SetCurrRangeCmd, CurrRangeKey: curr_range}
        msg_dict = self.send_cmd(cmd_dict)
        return msg_dict[ResponseKey][CurrRangeKey]


    def get_curr_range(self):
        """Gets the device's range setting for measuring working electrode current (uA).

        Returns:
            str : working electrode current range setting (from device), e.g., '10uA'

        """
        cmd_dict = {CommandKey: GetCurrRangeCmd}
        msg_dict = self.send_cmd(cmd_dict)
        return msg_dict[ResponseKey][CurrRangeKey]


    def get_all_curr_range(self):
        """Gets a list of all current ranges supported by the device.
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

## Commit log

2016-05-13 Project creation.
    [potentiostat.sch]
2016-05-13 Added ad8250 programmable instrumentation amplifier for scalable DAC output.
    [potentiostat.sch]
2016-05-14 Added +/- 15V supply for op amps. Added programmable gain amplifiers.
    [potentiostat.sch]
2016-05-14 More work on design.
    [potentiostat.sch]
2016-05-14 Further work on poteniostat circuit.
    [potentiostat.sch]
2016-05-15 Worked more on initial design added programmable gain transimpedance amplifier and expansion header.
    [potentiostat.sch]
2016-05-15 Added level shifter (0.6V) to output of transimpedance amplifier. Added note on what still needs to be done to complete the design.
    [potentiostat.sch]
2016-05-16 Added schottky diode and decoupling caps to TIA.
    [potentiostat.sch]
2016-05-17 Modified control amp schematic a bit to make it cleaner.
    [potentiostat.sch]
2016-05-19 Added note about switch arrangement.
    [potentiostat.sch]
2016-09-28 Worked on potentiostat design.
    [potentiostat.sch]
2016-09-29 Enlarged schematic sheet for addition of 10V reference and differential amplifier.
    [potentiostat.sch]
2016-09-30 Finished initial schematic layout. Component values assigned. Passes DRC.
    [potentiostat.sch]
2016-09-30 Added second optional expasion header, i2c pullups and 2nd electrode connector.
    [potentiostat.sch]
2016-10-01 Worked on footprint assignments.
    [BOM.xls, potentiostat.kicad_pcb, potentiostat.sch]
2016-11-16 Worked on footprint assignment.
    [BOM.xls, potentiostat.sch]
2016-11-17 Finished footprint assignment. Worked on PCB layout.
    [potentiostat.sch]
2016-11-19 Worked on pcb layout.
    [potentiostat.kicad_pcb]
2016-11-20 Finished intial routing of pcb.
    [potentiostat.dsn, potentiostat.kicad_pcb]
2016-11-21 Renamed hardware/pcb sub-directory hardware/teensy_shield.
    [BOM.xls, potentiostat.dsn, potentiostat.kicad_pcb, potentiostat.sch]
2016-11-21 Added dummy test cell design.
    [dummy_cell.kicad_pcb, dummy_cell.sch]
2016-11-21 Cleaned up silkscreen and created gerber files.
    [potentiostat-B_Cu.gbl, potentiostat-B_Mask.gbs, potentiostat-B_SilkS.gbo, potentiostat-Edge_Cuts.gbr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]
2016-11-21 Added gerber files for dummy cell. Added zip archives of gerber files.
    [dummy_cell-B_Cu.gbl, dummy_cell-B_Mask.gbs, dummy_cell-B_SilkS.gbo, dummy_cell-Edge_Cuts.gbr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]
2016-12-01 Worked on BOM.
    [BOM.xls, potentiostat.sch]
2016-12-02 Finished initial version of BOM.
    [BOM.xls]
2016-12-05 Added dummy cell simulations - for component selection.
    [BOM.xls]
2016-12-13 Modified dummy_cell simulation. Add pdf of schematic.
    [BOM.xls]
2016-12-13 Added hgignore file. Added initiall aout test firmware.
    [potentiostat.sch]
2016-12-22 Fixed issues schematic. Added new parts to layout. Updated BOM. Board not yet re-routed.
    [BOM.xls, BOM_turnkey.xls, potentiostat.dsn, potentiostat.kicad_pcb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]
2016-12-23 Re-routed board and created new gerber files.
    [potentiostat-B_Cu.gbl, potentiostat-B_Mask.gbs, potentiostat-B_SilkS.gbo, potentiostat-Edge_Cuts.gbr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]
2017-01-03 Modified teensy shield BOM, layout, and gerbers per pcb manufacturers suggestions.
    [BOM.xls, BOM_turnkey.xls, potentiostat-B_Cu.gbl, potentiostat-B_Mask.gbs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]
2017-01-07 Worked on analog subsystem firmware.
    [BOM.xls, BOM_turnkey.xls, potentiostat.sch]
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2017-03-28 Finished initial version of enclosure design.
    [enclosure.dxf, enclosure_assembly.scad, enclosure_projection.dxf, enclosure_projection.scad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]
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2017-03-28 Worked on laser cutting layout.
    [layout_single.dxf]
2017-03-31 Added fullsheet and fullsheet-split laser cutting jobs (layout + gcode) for acylic enclosure.
    [layout_fullsheet.dxf]
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2017-04-09 Rearranged hardware directory structure a bit.
    [BOM.xls, BOM_turnkey.xls, dummy_cell-B_Cu.gbl, dummy_cell-B_Mask.gbs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]
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2017-10-24 Added standoffs part numbers to acrylic enclosure dxf.
    [enclosure.dxf]
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2018-01-18 Added part substitution for ADG441BRZ-REEL to BOM.
    [BOM.xls, BOM_turnkey.xls]
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2018-07-16 Added initial schematic design for 7-channel make-before-break multiplexer expansion board.
    [multiplexer.kicad_pcb, multiplexer.sch]
2018-07-17 Finished initial layout and routing of make-before-break multiplexer expansion board.
    [multiplexer.dsn, multiplexer.kicad_pcb, multiplexer.sch]
2018-07-19 Added BOM.txt and gerber files.
    [multiplexer-B_Cu.gbl, multiplexer-B_Mask.gbs, multiplexer-B_SilkS.gbo, multiplexer-Edge_Cuts.gbr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]
2018-08-06 Modified lasercutting for test_base again - to fit on acrylic.
    [test_base.dxf]
2018-08-06 Added base design for testing multiplexer.
    [test_base.dxf]
2018-08-06 Added lasercutting gcode for test_base design.
    [test_base.dxf]
2018-08-06 Modified lasercutting files - shifted position.
    [test_base.dxf]
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2018-12-19 Modified teensy footprint - added missing hole for pin between pins 50 and 51. Modified silkscreen changed +/-15V to +/-12V.
    [potentiostat.kicad_pcb]
2018-12-19 Modified schematic. Changed +/-15V DC-DC converter to +/-12V DC-DC converter. Changed net labels accordingly. Remade netlist, etc.
    [BOM.xls, BOM_turnkey.xls, potentiostat-B_Cu.gbl, potentiostat-B_Mask.gbs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]
2018-12-19 A few more minor changes to kicad layout doc.
    [potentiostat.kicad_pcb]
2018-12-20 Added notes to turnkey BOM.
    [BOM_turnkey.xls]
2018-12-24 Fixed qty issues for items #1 and #6 in BOM.
    [BOM.xls, BOM_turnkey.xls]
2018-12-24 Minor changes to kicad pcb gui config.
    [potentiostat.kicad_pcb]
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2019-01-16 Added second version of multiplexer design. Removed screw terminals for electrodes and replaced with 5x2 shrouded header - the idea being that screw terminals or 3-pin electrode headers can be added 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
    [multiplexer-B_Cu.gbl, multiplexer-B_Mask.gbs, multiplexer-B_SilkS.gbo, multiplexer-Edge_Cuts.gbr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]
2019-01-16 Worked on adapter pcbs for multiplexer.
    [adapter.kicad_pcb, adapter.sch, multiplexer.kicad_pcb]
2019-01-18 Modified v0.2 of multiplexer. Extended tab with 5x2 header connector to deal with interference issue. Finished the two initial multiplexer adapter pcbs - mux_to_term and mux_to_3pin.
    [adapter-B_Cu.gbl, adapter-B_Mask.gbs, adapter-B_SilkS.gbo, adapter-Edge_Cuts.gbr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]
2019-01-21 Final checkin before order prototypes of multiplexer_v2, mux_to_3pin and mux_to_term pcbs.
    [adapter-B_Cu.gbl, adapter-B_Mask.gbs, adapter-B_SilkS.gbo, adapter-Edge_Cuts.gbr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]
2019-01-21 Modified dimension callouts on multiplexer_v2.
    [multiplexer.kicad_pcb]
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2019-03-22 Added new lasercut enclosure design for rodeostat + multiplexer.
    [enclosure.dxf]
2019-03-24 Added lasercutting files for multiplexer enclosure.
    [enclosure.dxf]
2019-04-10 Fixed issue with multiplexer enclosure laser cutting file.
    [enclosure.dxf]
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2019-05-02 Renamed multiplexer directories.
    [multiplexer-B_Cu.gbl, multiplexer-B_Mask.gbs, multiplexer-B_SilkS.gbo, multiplexer-Edge_Cuts.gbr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]
2019-05-14 Added fullsheet and 2nd one part cutting jobs for multiplexer enclosure.
    [enclosure.dxf, test_base.dxf]
2019-05-31 Added fullsheet cutting job for multiplexer enclosure.
    [enclosure.dxf]
2021-01-25 added version number to teensy_shield sub-directory.
    [BOM.xls, BOM_turnkey.xls, potentiostat-B_Cu.gbl, potentiostat-B_Mask.gbs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]
2021-02-01 Worked on version 0.2 design.
    [BOM.xls, BOM_turnkey.xls, potentiostat.dsn, potentiostat.kicad_pcb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]
2021-02-02 Worked on version 0.2 of teensy shield.
    [potentiostat.sch]
2021-02-03 Worked on version 0.2 of teensy pcb.
    [potentiostat.sch]
2021-02-04 Worked on revision 0.2 of teensy pcb.
    [potentiostat.sch]
2021-02-04 Finished initial draft of version 0.2 of teensy pcb.
    [potentiostat.sch]
2021-02-07 Worked on teensy shield version 0.2. Ported footprints from .mod to .kicad_mod. Finished initial footprint assignments.
    [potentiostat.kicad_pcb, potentiostat.sch]
2021-02-07 Work on layout of teensy pcb version 0.2
    [potentiostat.kicad_pcb, potentiostat.sch]
2021-02-08 Finished initial layout for version 0.2 of teensy pcb.
    [potentiostat.kicad_pcb, potentiostat.sch]
2021-02-09 Completed initial routing of PCB.
    [potentiostat.dsn, potentiostat.kicad_pcb, potentiostat.sch]
2021-02-16 Added new BOMs.
    [BOM.xls, BOM_FULL.xlsx, BOM_JLCPCB.xlsx, BOM_turnkey.xls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]
2021-02-17 Added gerber files for new version. Added cpl file for assembly.
    [CPL_JLCPCB.xlsx, potentiostat-B_Cu.gbl, potentiostat-B_Mask.gbs, potentiostat-B_Paste.gbp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]
2021-02-17 Worked on bom and cpl files.
    [BOM_JLCPCB.xlsx, CPL_JLCPCB_adjusted_angles.xlsx]
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2021-04-03 Modified R33 resistor value which caused gain error, for transimpedance amplifier in first prototypes of V0.2 design.
    [BOM_FULL.xlsx, BOM_JLCPCB.xlsx, potentiostat.kicad_pcb, potentiostat.sch]
2021-04-05 Fixed quantities in BOM after component change.
    [BOM_FULL.xlsx, BOM_JLCPCB.xlsx]
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2023-01-26 Fixed footprint issue with mx design.
    [potentiostat.dsn, potentiostat.kicad_pcb, potentiostat.sch]
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2023-02-23 Fixed error in high current mx fab BOM.
    [RSTAT_MX_HC_BOM_JLCPCB.xlsx]
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
